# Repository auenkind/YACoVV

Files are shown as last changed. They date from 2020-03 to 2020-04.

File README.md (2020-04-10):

# YACoVV - Yet Another (SARS-)CoV(-2)Ventilator

[German-Version is more Detailed / updated more frequently](README_DE.md) <- Please translate (see Contributing)!

[Version française](README_FR.md)

[Spanish Version](README_ES.md)

This project aims at constructing components for the production of ventilators that can be used as last-resort-solutions for SARS-CoV-2 patients. 

All components should be constructed with parts, raw materials and skills needed in the places in which the devices come into use. 

The most complex component of a ventilator is the correct, reliable and safe pressure control of the ventilator as well as keeping the positive end-expiratory pressure intact. Currently, there is a promising solution for the pressure control that has already been transferred into a functioning sample.

The components are:
- [Pressure regulator and timing](#Pressure%20regulator)
    - Regulation of the ventilation pressure
    - Upholding the modifiable PEEP
    - Regulation of modifiable Breath Frequency
    - Regulation of modifiable I:E relation
- [Monitoring](MONITORING_DE.md) (please Translate!)
    - Measurement of volume
    - Measurement of pressure
    - Measurement of frequency
- [Respiratory gas/ Processing](#Breath%20gas%20production)
    - ozone/oxygen mixture
    - Recovery
        - Co2-absorber 
    - Heating 
    - Humidification

[miro-Board](https://miro.com/app/board/o9J_kuxCsRI=/) (Idea and Link Collection)

## Pressure regulator

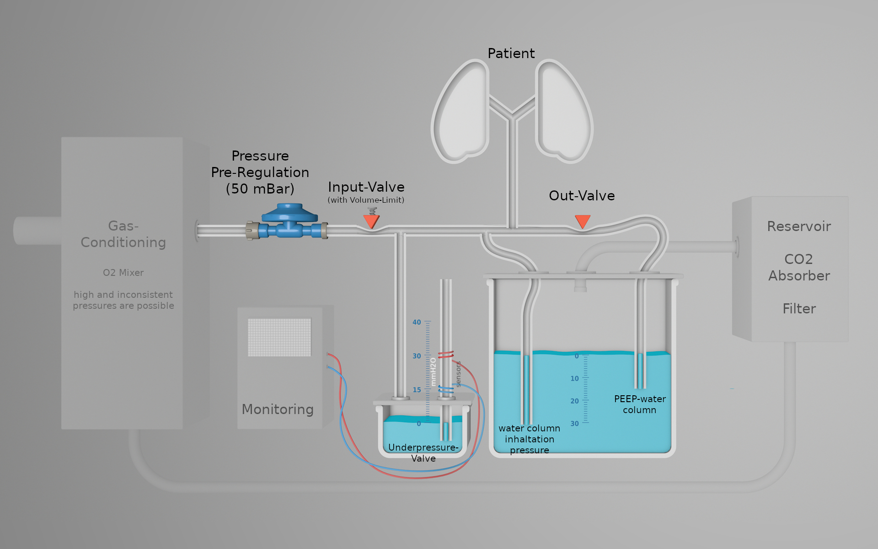
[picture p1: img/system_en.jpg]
Regulator-parts (https://www.youtube.com/watch?v=yE1sUh0wc-A)


[Animation](https://www.youtube.com/watch?v=yE1sUh0wc-A)

### Functional principle

The concept behind the [water column](https://de.wikipedia.org/wiki/Meter_Wassers%C3%A4ule) makes sure pressure regulation functions. To generate modifiable pressures in the system, tubes are immersed into water appropriate to the desired pressure. The control tubes are simultaneously used as relief valve. Underpressure in the system is prevented by a additional small water column. This column also allows breathing of room air.

Because high entrance pressures can only be regulated through this system with very precise component, we decided using a [50 mBar gas pressure regulator](https://www.campingaz.com/DE/p-25990-verstellbarer-regler-30-50-mbar.aspx) to pre-regulate the pressure. These regulations are available all over the world.

We are using the basic principle behind [constriction hose-valves](https://www.ako-armaturen.de/produkte/mechanische-schlauchquetschventile.html) for our valves since these can be easily manufactured out of widely available components. On top of that, these kinds of valves bear the advantage that all components that come into contact with contaminated gas can be replaced. 

#### Inhalation
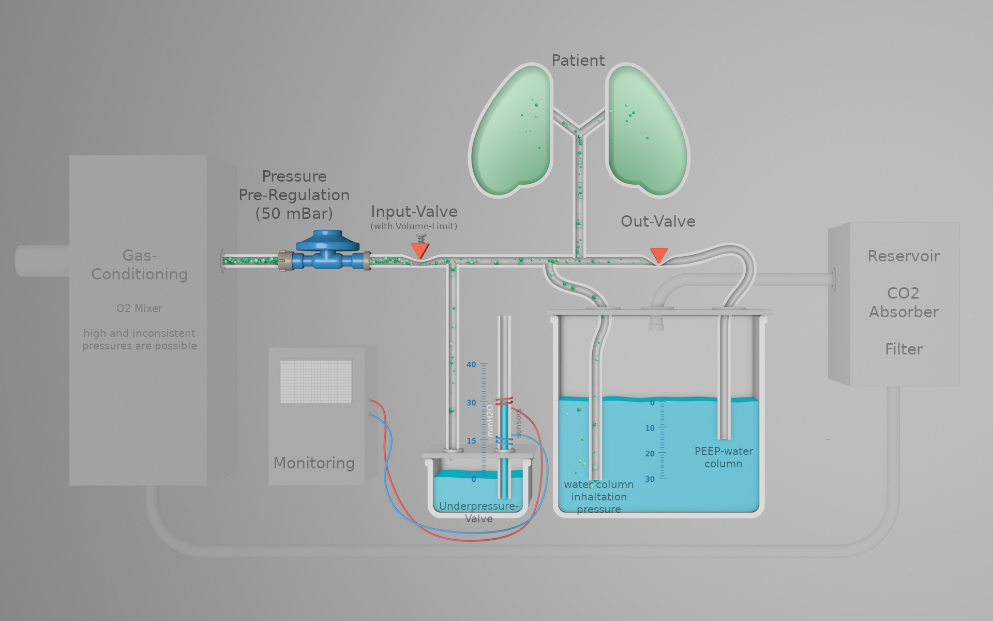
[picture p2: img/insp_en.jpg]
inhalation


- The input pressured is reduced to ~ 50 mBar by a [mechanical pressure regulator](https://www.campingaz.com/DE/p-25990-verstellbarer-regler-30-50-mbar.aspx)
- The input valve is opened mechanically. A adjustment screw limit flow-volume. Due to the adjustment screw valves without regulating funtions can be used and gas-loss through the limiting water column is minimized.
- Gas flows towards the patent until the pressure reaches the level set by the wate column. 
#### Exhalation
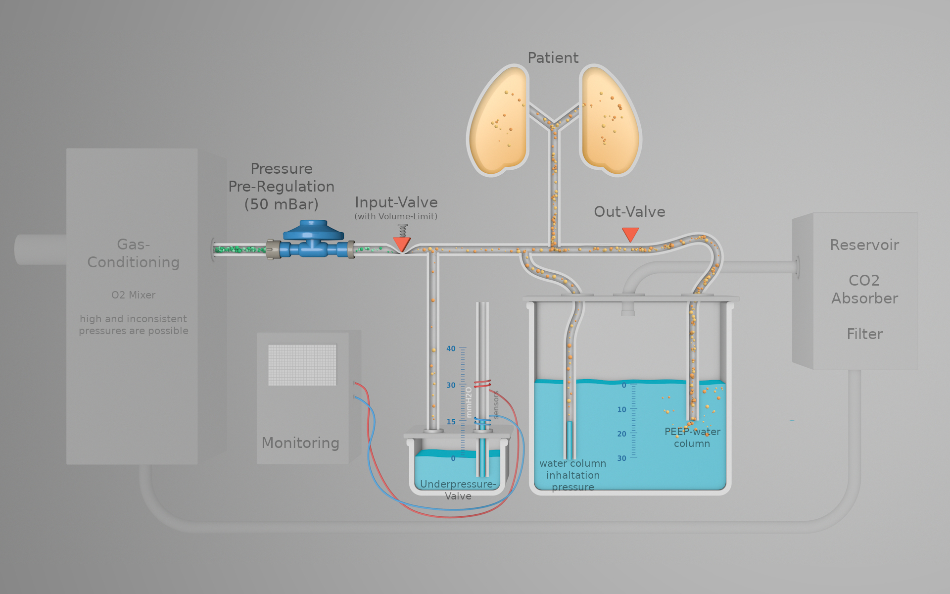
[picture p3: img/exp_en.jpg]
exhalation

- The input valve is closed and the output valve opened
- Gas flows from the patient through the PEEP water column into the reservoir
- PEEP can be adjusted by mofing the water column

#### System-Safety
- Over-Pressurizing is practically impossible in the system as the pressure is only closed by water columns. No mechanical parts restrict the pressure.
- There are no mechanical parts that cna get stuck
- Losing PEEP is only possible when there are leaks
- The underpressure water column allows the patient to breath room air. This water column also prevnts any underpressure buildup in the system,

#### Valve-Control and Timing

The timing currently functions through a microcontroller and two servos. This solution will replaced with the motor of a windscreen wiper with two [camdiscs](https://en.wikipedia.org/wiki/Cam).

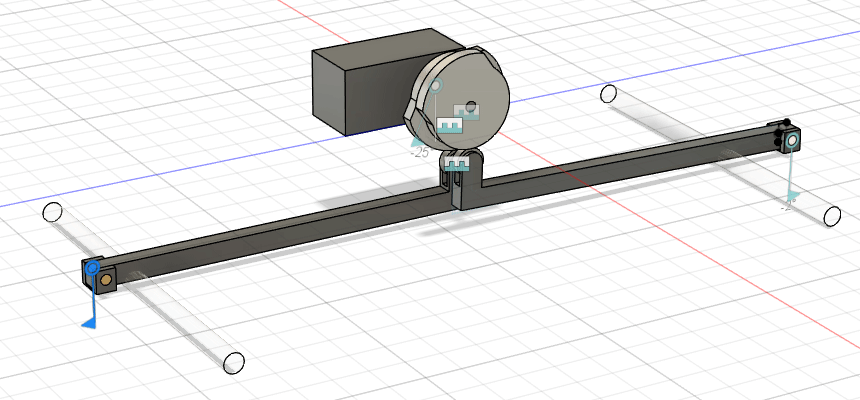
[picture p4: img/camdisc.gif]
Camdiscs (https://autode.sk/3dx6EbZ)


[Camdisc Animation](https://autode.sk/3dx6EbZ)

### Functional Prototype

Prototype (https://www.youtube.com/watch?v=eBIlyaHW4l0)

Problems with this prototype:
- [Lack of check valves](https://github.com/auenkind/YACoVV/issues/3)
- [Air bubbles in discharge hose too big](https://github.com/auenkind/YACoVV/issues/1)
- [Servo/Microtroller](https://github.com/auenkind/YACoVV/issues/2)

## Breath gas production
This component reuses the exhaled breath gas. Co2 is absorbed and oxygen is mixed in.

## Contributing
We are happy about every contribution to this project! We need action NOW! Please don’t overthink your contribution, join us!

If these projects’ solutions win prizes in competitions such as the [Code Life Ventilator Challenge](https://www.agorize.com/en/challenges/code-life-challenge?lang=en), we will use the money to construct the components or improve the design.

Things everyone can do:
- Translation of the README_DE.md in as many languages as possible. Translations will have be adjusted very frequently, changes should quickly be translated.
- Construct a YACoVV und run it! Feedbacks on the materials used and problems that have come up would be awesome!
- Take on one of the concrete problems in the issue section.

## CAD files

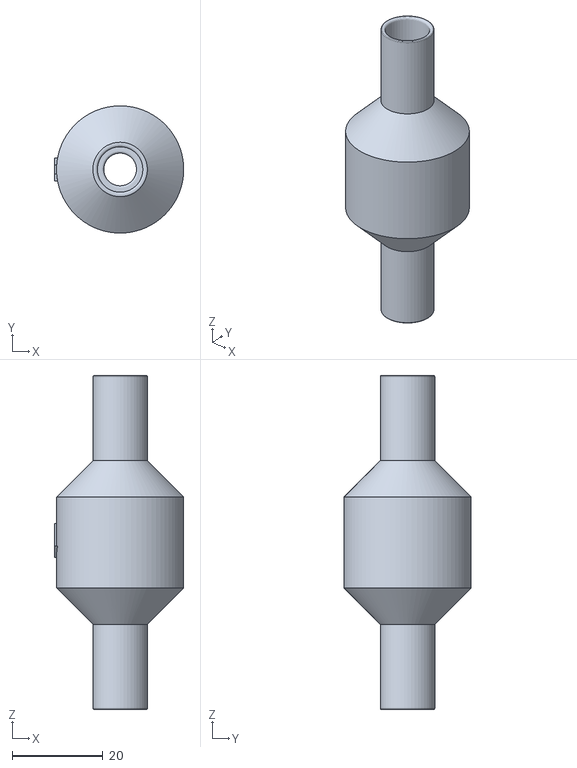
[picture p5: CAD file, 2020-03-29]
3d_print_models/check_valve/body.stl
28.5 x 28.0 x 73.5

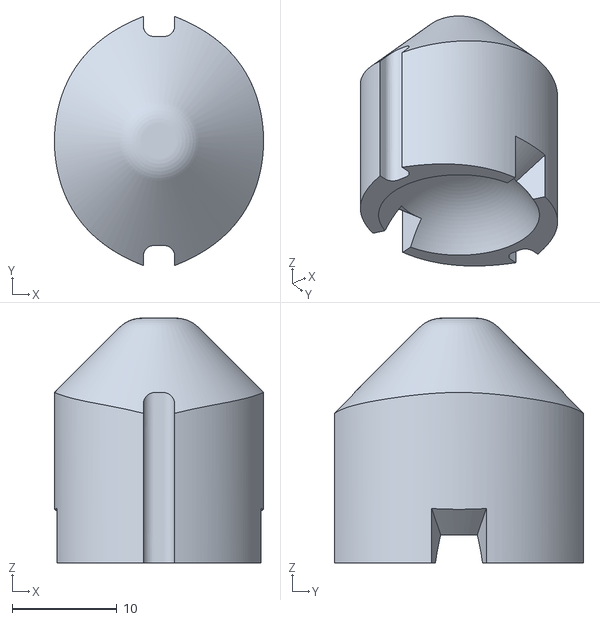
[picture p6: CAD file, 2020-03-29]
3d_print_models/check_valve/bulb.stl
20.0 x 23.8 x 23.4

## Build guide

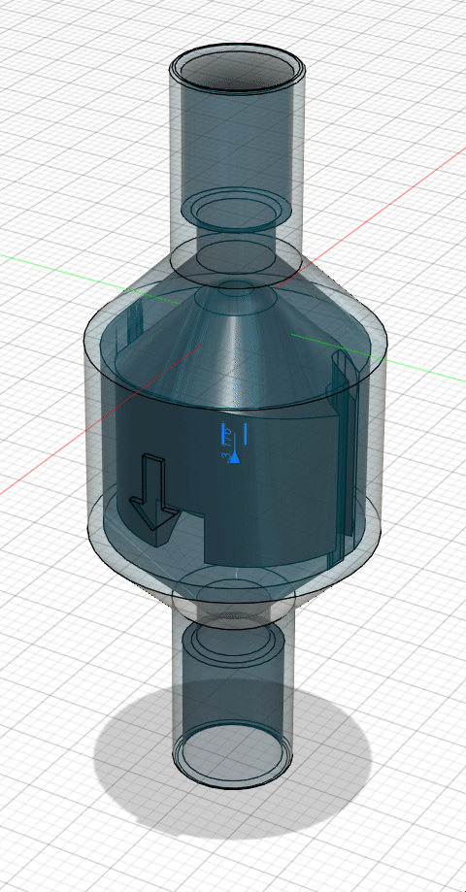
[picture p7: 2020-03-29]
3d_print_models/check_valve/animation.gif

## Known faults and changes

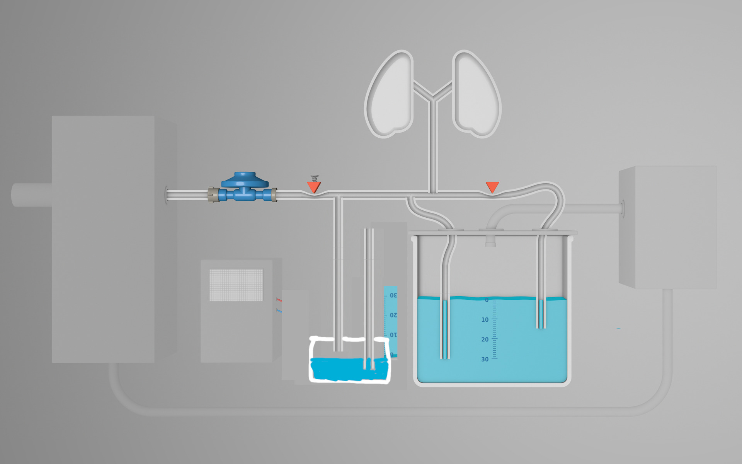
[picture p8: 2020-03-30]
img/infogfx_changes.jpg

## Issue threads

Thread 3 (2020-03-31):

### ISSUE TITLE
Rückschlagventile

### ISSUE THREAD

**Issue by auenkind** [auenkind/YACoVV#3]
Der Druckregler braucht 3 Rückschlagventile an den Wassersäulen so das kein Wasser in das System gelangen kann.

**Comment by dachdecker2** [comment]
Könnte es helfen, statt einem Rückschlagventil eine Druckbegrenzung nach unten einzubauen?

Mein Vorschlag ist, einen zweiten Wasserbehälter (links im Bild) - invers zum ersten angeschlossen (rechts im Bild) - zu benutzen:
 - der Patient ist über der Wasseroberfläche angeschlossen (Wie der CO2-Absorber im bestehenden Teil des Systems)
 - Umgebungsluft ist am im Wasser steckenden Schlauch angeschlossen

Die Eintauchtiefe bestimmt den Mindestdruck - der sollte unter p_a liegen. 
Der Schlauch zur Umgebungsluft müsste außerdem lang (bzw. hoch) genug sein, damit das Wasser nicht aus dem Behälter gedrückt werden kann - d.h. mehr als die Eintauchtiefe p_i (oder gleich > 50 mbar).

![Rueckschlagventilersatz](https://user-images.githubusercontent.com/3836508/77819958-1aed5200-70df-11ea-8b76-93d760189531.gif)

**Comment by GRRTK** [comment]
Kann man Rückschlagventile aus der Aquaristik nehmen? z.B. [das hier](https://www.interaquaristik.de/aquascaping/glaswaren/co2-zubehoer/orinocoglass-check-valve-rueckschlagventil-aus-glas/a-83653) oder [das hier](https://www.koigarten-mueller.de/Luft-Rueckschlagventile-4mm-mit-Membrane)?

**Comment by Pixtxa** [comment]
Könnte man so evtl. ein Ventil einsparen? Wenn da hinten dran Wasser ist, kann das ja eh nur wieder abfließen, welchen Weg es nimmt, dürfte egal sein.
Das Ventil fürs Manometer würde ich nicht auch so einsparen, da es den Messwert verfälschen würde, wenn dort Wasser hineinfließt oder herausgesaugt wird.
![Screenshot_20200329_043327](https://user-images.githubusercontent.com/30337073/77838757-0361a800-7177-11ea-914b-e75fbb08f565.jpg)

Alternativ müsste sich aber auch ein Behälter mit eingetauchtem Schlauch (Patient wird an abgedichteten Deckel des Gefäßes angeschlossen) als Unterdruck-Ventil verwenden lassen. Da dieses dann sofort Luft einströmen lässt, falls der Patient beim Husten einatmet, kann die Wassersäule in den anderen Schläuchen nicht so weit steigen, dass sie gefährlich werden könnte.
![Screenshot_20200329_050353](https://user-images.githubusercontent.com/30337073/77839168-b97ac100-717a-11ea-930b-836886c852d7.jpg)

**Comment by auenkind** [comment]
> 
> 
> Kann man Rückschlagventile aus der Aquaristik nehmen? z.B. [das hier](https://www.interaquaristik.de/aquascaping/glaswaren/co2-zubehoer/orinocoglass-check-valve-rueckschlagventil-aus-glas/a-83653) oder [das hier](https://www.koigarten-mueller.de/Luft-Rueckschlagventile-4mm-mit-Membrane)?



> 
> 
> Kann man Rückschlagventile aus der Aquaristik nehmen? z.B. [das hier](https://www.interaquaristik.de/aquascaping/glaswaren/co2-zubehoer/orinocoglass-check-valve-rueckschlagventil-aus-glas/a-83653) oder [das hier](https://www.koigarten-mueller.de/Luft-Rueckschlagventile-4mm-mit-Membrane)?

Das ist grundsätzlich das richtige Ventilprinzip, die Aquaristik-Ventile haben aber einen deutlich zu kleinen Durchmesser um die benötigte Durchflussmenge / Zeit zu erreichen.

**Comment by auenkind** [comment]
> 
> 
> Könnte es helfen, statt einem Rückschlagventil eine Druckbegrenzung nach unten einzubauen?
> 
> Mein Vorschlag ist, einen zweiten Wasserbehälter (links im Bild) - invers zum ersten angeschlossen (rechts im Bild) - zu benutzen:
> 
>     * der Patient ist über der Wasseroberfläche angeschlossen (Wie der CO2-Absorber im bestehenden Teil des Systems)
> 
>     * Umgebungsluft ist am im Wasser steckenden Schlauch angeschlossen
> 
> 
> Die Eintauchtiefe bestimmt den Mindestdruck - der sollte unter p_a liegen.
> Der Schlauch zur Umgebungsluft müsste außerdem lang (bzw. hoch) genug sein, damit das Wasser nicht aus dem Behälter gedrückt werden kann - d.h. mehr als die Eintauchtiefe p_i (oder gleich > 50 mbar).
> 
> ![Rueckschlagventilersatz](https://user-images.githubusercontent.com/3836508/77819958-1aed5200-70df-11ea-8b76-93d760189531.gif)
> 
> Nachtrag:
> der Vorschlag hätte folgende Vorteile gegenüber Rückschlagventilen:
> 
>     * spontanes Einatmen wird nicht übermäßig behindert
> 
>     * weiterhin keine verschleisbehafteten/verhaltensbeeinflussenden Teile
> 
> 
> richtige Rückschlagventile kann man vielleicht zusätzlich einbauen, diese machen das Systemverhalten aber wahrscheinlich komplizierter:
> 
>     * Öffnungsverhalten und zusätzlicher ggf. nich konstanter Druckabfall über den Ventilmechanismus
> 
>     * Verhaltensänderung bei Benetzung mit Wasser

Das ist eine sehr gute Überlegung. Bedenken muss man dabei noch die verhältnismäßig große Volumensteigerung des Überdrucksystems durch den "Hohlraum" im zweiten Behälter.

**Comment by dachdecker2** [comment]
Man müsste mal probieren, ob das zusätzliche Luftvolumen wirklich groß sein muss. Intuitiv hätte ich z.B. das Luftvolumen im Video gezeigten Glasbalon sehr viel größer gemacht - offensichtlich funktioniert es aber auch mit dem Volumen << 1 l schon.
"Worst-Case-Betrachtung":
Der Druck im System kann sich eigentlich nicht um mehr als 50 mbar ändern - das sind etwa 5% des Luftdrucks. Nach Wikipedia soll das Tidalvolumen ~0,5 l sein. Wenn Die Regelung keine Schwierigkeiten mit dem größeren Volumen in Schlauch und "Ventil" hat, ergibt sich ein Verlust an bis zu 20% des bereitgestellten Gases unter folgenden Annahmen:
- Ventilvolumen: 1 l
- Schlauchvolumen: 1 l
- Druckänderung zwischen Ein- und Ausatmen: bis zu 50 mbar
- Umgebungsdruck: 1000 mbar
- Tidalvolumen: 0,5 l
- Gasverlust = Umgebungsdruck * Tidalvolumen / (Druckänderung * (Ventilvolumen + Schlauchvolumen) ) = 0,2

Angesichts des überaschend kleinen Tidalvolumens würde ich als Gegenvorschlag zur Elimination eines Ventils (@Pixtxa) die Veringerung des Totvolumens vorschlagen (siehe Bild), damit die angeschlossene Person weniger ausgeatmete Luft zurückbekommt.
![Rueckschlagventilersatz2](https://user-images.githubusercontent.com/3836508/77861356-bb915e00-7214-11ea-9a57-eab599d56221.png)

**Comment by auenkind** [comment]
@dachdecker2 deine letzte Zeichnung ist eine wirklich gute Lösung, ich werde das so in die Zeichnungen übernehmen. Zusätzlich dazu können wird dann unser Schlauchmanometer einsparen. Denn der Druck wird an der Wassersäule angezeigt die im linken Schlauch des neuen Wassergefäßes steht. Nebenbei ergibt sich noch der Vorteil das diese Wassersäule doppelt so hoch steigt wie die im bisherigen Aufbau und dadurch besser abzulesen ist.

**Comment by auenkind** [comment]
würde in etwa so aussehen:

![infogfx_changes](https://user-images.githubusercontent.com/13538227/77882566-85c69680-7261-11ea-9af2-22baef322b6a.jpg)

**Comment by sneu14** [comment]
ich denke auch das diese Lösung als Unterdruckventil funktioniert. Ob man das auch als Manometer verwenden kann müsste man testen. Durch das zusätzliche Luftvolumen in dem Behälter könnte die Anzeige etwas mehr schwingen wie wenn es direkt angeschlossen ist. Das sollten wir aber auf jeden Fall testen

**Comment by dachdecker2** [comment]
@auenkind, @Pixtxa : genau so habe ich das gemeint. Was meint Ihr zum Totvolumen im Schlauch? Wie groß ist das im Video gezeigte Tidalvolumen?

**Comment by sneu14** [comment]
Zum Totavolumen sollten wir uns mal die Hardware anschauen die unmittelbar am Patienten verwendet wird. Im besten Falle würden man 2 Schläuche bis unmittelbar zum Patienten legen. Dann haben wir in den Leitungen den Luftstrom immer nur in einer Richtung, andererseits erhöhen wir dadmit das Volumen des gesamten Systems und müssen viel mehr Luft reinblasen um den Druck zu erreichen. Ich denke wir müssen uns dort an den Beatmungsgarnituren orienteiern die verfügbar sind auch verwendet werden würden und diese so nah wie möglich an unserem System anschliessen.

**Comment by auenkind** [comment]
ich schließe das, denn die aktuell Rückschlagventil Lösung erscheint mir brauchbar. Wenn es im Test nicht klappen sollte mache ich das Ticket wieder auf,

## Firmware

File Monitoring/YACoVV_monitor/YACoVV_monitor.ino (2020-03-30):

/* This is a very simple program for the monitoring the manometer of YACoVV
 *  https://github.com/auenkind/YACoVV
 *  
 *  The current state of code is only for prototyping, so don't use it with an patient is connected to your system.
 *  
 *  The state of the inputs and the calculated breathing frequency is written to the serial Port ans can be plotted with
 *  the "Serial Plotter" of the Arduino IDE
 *  
 *  The state of the system is reported with a stripe of WS2812 LEDs. See defines below for pin configuration.
 *  A momentary switch needs to be connected to reset the system from error state.
 *  
 *  On normal operation the LEDs are set to red. If the system starts working correctly and the frequencys for inhalation are exhalation
 *  are nearly the same, the LED changes to blue and blinks an every breathing cycle. If an error occurs, the LED color changes to red.
 *  If you press the button the LEDs changes to green an remains in this state until the next error occurs.
 */

#include <CapacitiveSensor.h>
#include <Adafruit_NeoPixel.h>

#define PIN_WS2812_LEDS   7
#define NUM_WS2812_LEDS   3
#define PIN_UPPER_SENSOR  2
#define PIN_LOWER_SENSOR  3
#define PIN_SWITCH        6
#define F_TIMEOUT         5000


#define OFF   0
#define GREEN 1
#define BLUE  2
#define RED   3

Adafruit_NeoPixel pixels(NUM_WS2812_LEDS, PIN_WS2812_LEDS, NEO_GRB + NEO_KHZ800);


int errorcommited = 0;
int errorcount = 0;
boolean ledstate = 0;
int state_a;
int state_b;

int state_a_prev;
int state_b_prev;

float freq_exsp = 0;
float freq_insp = 0;
long f_start_exsp;
long f_start_insp;

void setLed(int color) {
  pixels.clear();
  for (int i = 0; i < NUM_WS2812_LEDS; i++) {
    switch (color) {
      case OFF:
        pixels.setPixelColor(i, pixels.Color(0, 0, 0));
        break;
      case GREEN:
        pixels.setPixelColor(i, pixels.Color(0, 255, 0));
        break;
      case BLUE:
        pixels.setPixelColor(i, pixels.Color(0, 0, 255));
        break;
      case RED:
        pixels.setPixelColor(i, pixels.Color(255, 0, 0));
        break;
    }
    pixels.show();
  }
}

void setup()
{
  pinMode(PIN_UPPER_SENSOR,INPUT_PULLUP);
  pinMode(PIN_LOWER_SENSOR,INPUT_PULLUP);
  pinMode(PIN_SWITCH, INPUT_PULLUP);
  Serial.begin(115200);
  pixels.begin();
  setLed(RED);
}

void loop()
{
  //Read values from Sensors
  state_a = digitalRead(PIN_UPPER_SENSOR);
  state_b = digitalRead(PIN_LOWER_SENSOR);

  //Print frequencys in breathes per minute and states of sensors
  Serial.print(freq_exsp * 60);
  Serial.print("\t");
  Serial.print(freq_insp * 60);
  Serial.print("\t");
  Serial.print(state_a);
  Serial.print("\t");
  Serial.println(state_b);

  // Calculate frequency of upper sensor when input changes from low to high
  if ( state_a > state_a_prev ) {
    freq_exsp = (float)1000 / ((float)millis() - (float)f_start_exsp);
    f_start_exsp = millis();
  }
  // Calculate frequency of lower sensor when input changes from low to high
  if ( state_b > state_b_prev ) {
    freq_insp = (float)1000 / ((float)millis() - (float)f_start_insp);
    f_start_insp = millis();
  }

  // Set frequency on upper sensor to zero if sensor doesn't changed for F_TIMEOUT milliseconds
  if ( millis() - f_start_exsp > F_TIMEOUT) {
    freq_exsp = 0;
  }

  //Same fpr lower sensor
  if ( millis() - f_start_insp > F_TIMEOUT) {
    freq_insp = 0;
  }

  // If difference of frequency between inspiration and exspritaion is to big increase errorcounter
  if ( abs((freq_insp - freq_exsp) * 60) > 5) {
    errorcount++;
  } else {
    errorcount = 0;
  }

  // If errorcounter is > 4 raise an alarm
  if (errorcount > 3 || (freq_insp == 0 && freq_exsp == 0)) {
    errorcommited = 0;
    setLed(RED);
  }
  // Reset error when system comes back again
  else {
    // On non error state let the led blink with every breathcycle.
    if (state_a_prev != state_a || state_b_prev != state_b){
    if (ledstate) {
      // Set the LED to green if error was commited by a user with the momentary switch
      if (errorcommited) {
        setLed(GREEN);
      }
      //If not commited switch led to blue
      else {
        setLed(BLUE);
      }
    } else {
      setLed(OFF);
    }
    ledstate = !ledstate;
    }
  }
  //Commit error when switch is pressed
  if (!digitalRead(PIN_SWITCH)) {
    errorcommited = 1;
  }

  state_a_prev = state_a;
  state_b_prev = state_b;
  delay(10);                             // arbitrary delay to limit data to serial port
}

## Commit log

2020-03-29 added animation of check-valve
2020-03-29 check valve changes
    [body.stl, bulb.stl]
2020-03-30 Create YACoVV_monitor.ino
    Added sample code for Monitoring
2020-03-31 Under pressure Valve now with water column
